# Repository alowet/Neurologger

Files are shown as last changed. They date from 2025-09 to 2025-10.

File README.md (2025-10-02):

## WILD: Wireless, Interactive, Lightweight Datalogger 

**WILD** (Wireless, Interactive, Lightweight Datalogger) is an open-source platform for **wireless, closed-loop electrophysiology and behavior monitoring** in freely moving small animals. It integrates high-density electrophysiology, optogenetic stimulation, an inertial measurement unit (IMU), ultrasonic microphone, and head-mounted camera into a lightweight system for **multi-modal recording**.

---

## 📌 Overview

- High-density neural recording  
- BLE-based wireless control and real-time monitoring  
- Closed-loop stimulation with DSP filtering and thresholds  
- SD-card logging in CE32 format with efficient data export  
- Windows GUI for device setup, live visualization, and data download  

---

## 📖 Documentation

Full documentation can be found here:

- [Installation](docs/install.md)  
- [Hardware](docs/hardware.md)
- [Usage Guide](docs/usage.md)  
- [Closed-loop Control](docs/closed-loop.md)
- [TinyML(Under development for supporting user-compiled models)](docs/tinyML.md)
- [File Format](docs/file-format.md)  
- [Development](docs/development.md)  

---

## 🖥 Quick start guide
WILD system board
WILD

Connector definitions
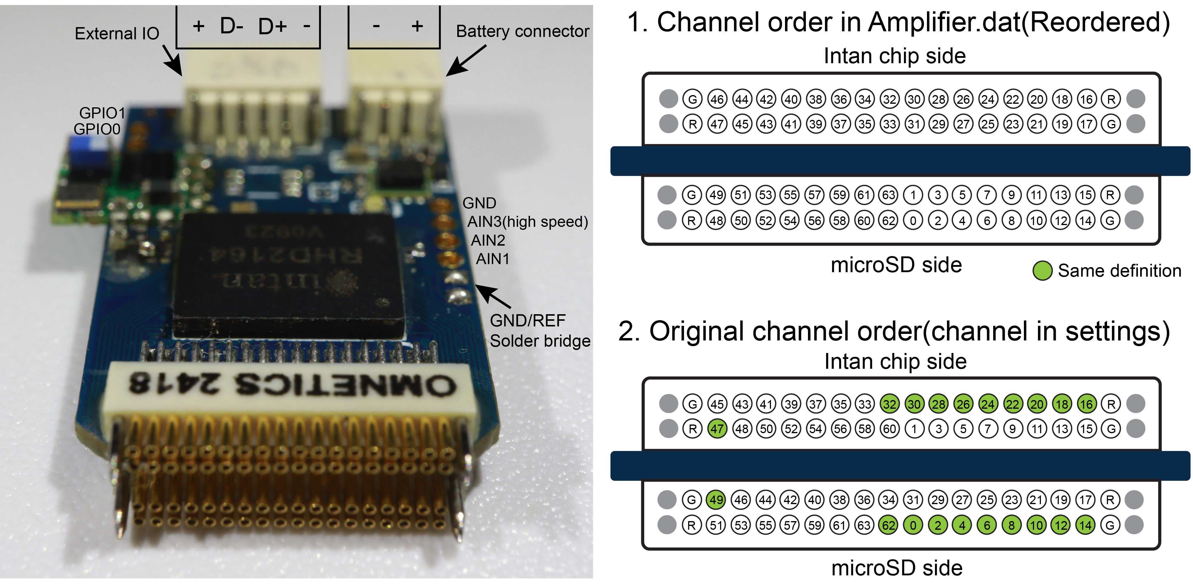
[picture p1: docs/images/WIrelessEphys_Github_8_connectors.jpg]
Connectors


WILD system diagram
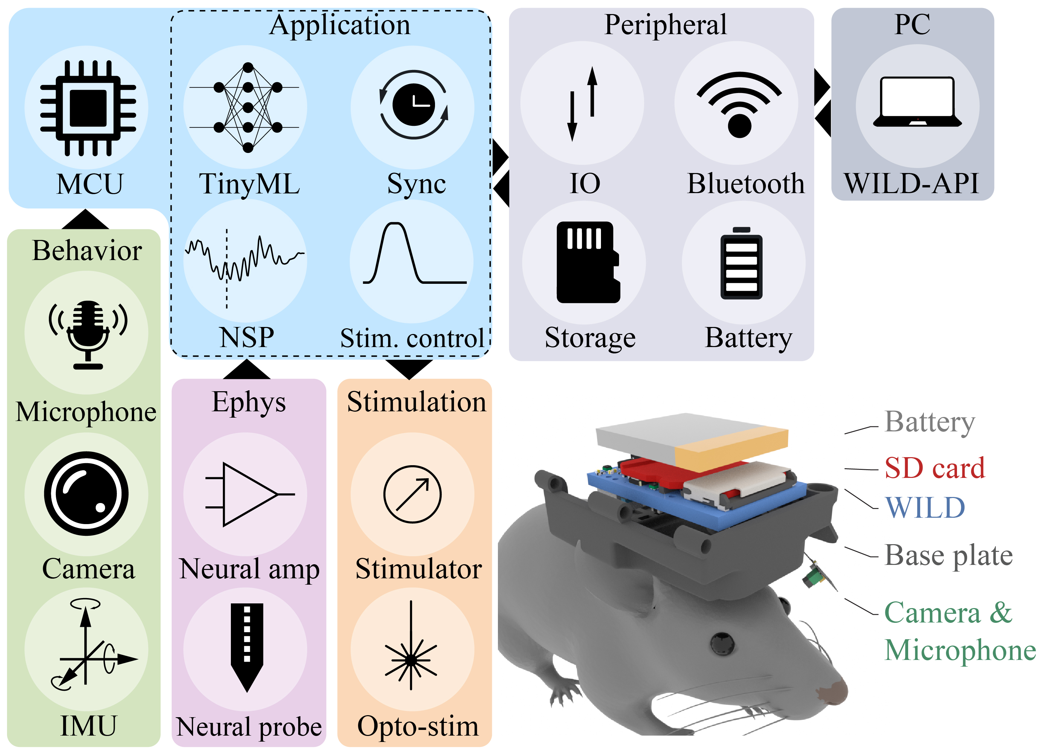
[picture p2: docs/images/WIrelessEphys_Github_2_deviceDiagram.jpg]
System schematics


### Device manufacturing
- PCB manufacturing and assembly (Gerber + BOM provided)
[Download here](https://github.com/ayalab1/Neurologger/tree/main/PCB)  
- Recommended PCB manufacturer: [NextPCB](https://www.nextpcb.com)
- 3D printed baseplate:   [Download here](https://github.com/ayalab1/Neurologger/tree/main/3Dprint)  

### Firmware programming (first time to empty MCU)
1. Connect 4-pin IO–USB cable (do not connect to PC yet).  
2. Short DFU model select pin to VDD(with a metal tweezer for shorting) to enter DFU mode.  
3. Connect USB cable to PC while shorting VDD and model select pin, once powered up, you can release the tweezer.  
4. In **STM32CubeProgrammer**, flash the bootloader firmware.  

### Preparing for recording
- Install WILD PC software:  
  [Download here](https://github.com/ayalab1/Neurologger/tree/main/Software)  
- Format microSD card in WILD PC software (CE32 format).
- Upload application image to SDcard, device will automatically upgrade during power-on from SDcard.
  [Download here](https://github.com/ayalab1/Neurologger/tree/main/Firmware)  
- Ensure battery is fully charged (check polarity on JST-SH2.0 connector).  

### Recording
- Ensure PC has Bluetooth 4.0+ enabled.  
- Connect wirelessly through GUI.  
- Start recording and monitor signals in real time.  

### Data downloading
- Use GUI **Download** function.  
- Files exported as: `amplifier.dat`, `analogin.dat`, `digitalin.dat`, `supply.dat`, `adc.dat`, `time.dat`, `info.rhd`, `CE_params.bin`.  
- Post-processing scripts including data formatting, video generation, sensor-fusions are provided.
[Download here](https://github.com/ayalab1/Neurologger/tree/main/Code)  
---

## ⚠️ Disclaimer

> DISCLAIMER – FOR INFORMATIONAL PURPOSES ONLY; USE AT YOUR OWN RISK  
>  
> The protocol content here is for informational purposes only and does not constitute legal, medical, clinical, or safety advice. Content added to protocols.io is not peer reviewed and may not have undergone formal approval. Information presented should not substitute for independent professional judgment. Any action you take using this information is strictly at your own risk. Neither the authors nor contributors are responsible for your use of the information.

---

## 🔧 Resources

- **Firmware & Embedded software**: Keil MDK, STM32CubeProgrammer  
- **PC GUI / API**: Visual Studio (C#)  
- **Machine learning integration**: Python, TensorFlow, ST Edge-AI  

---

## 📜 License

MIT License. See [LICENSE](LICENSE).

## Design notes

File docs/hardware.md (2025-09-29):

# Hardware

## WILD

## WILD opto-module

## WILD camera

## Cables
### Programming cable

### Sync cable

## microSD cards

## Batteries

## 3D print parts

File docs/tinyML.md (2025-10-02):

# Model-based computations(under development)
WILD supports online inference of pre-trained tensorflow-lite models.
Inference time is correlated to the model sizes.
Currently, the model is pre-compiled of the firmware, a run-time model loading mechanism is being developed.
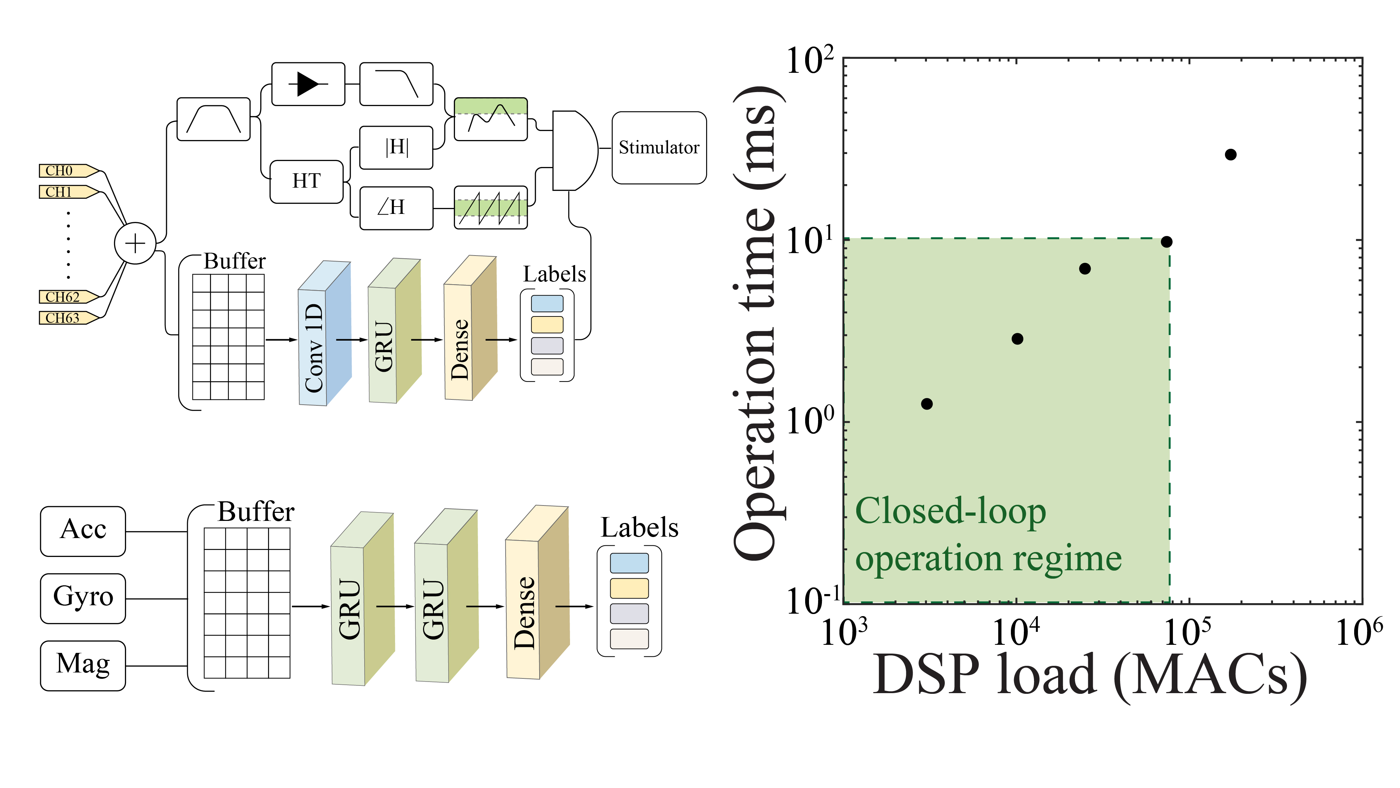
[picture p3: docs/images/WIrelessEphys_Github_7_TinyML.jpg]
TinyML


Sample scripts of model training/developing pipelines can be found here.

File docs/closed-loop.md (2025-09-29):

# Closed-loop Control

The system provides multiple DSP and stimulation modes for real-time closed-loop experiments.

## DSP Modes
- Disabled
- Single A
- Single A (Hilbert)
- Double
- Double (Hilbert)
- Cascade A→B
- Gated A & B
- Random
  
## Filters
One of the filter can be selected for one DSP channel (2 channels per system for now)
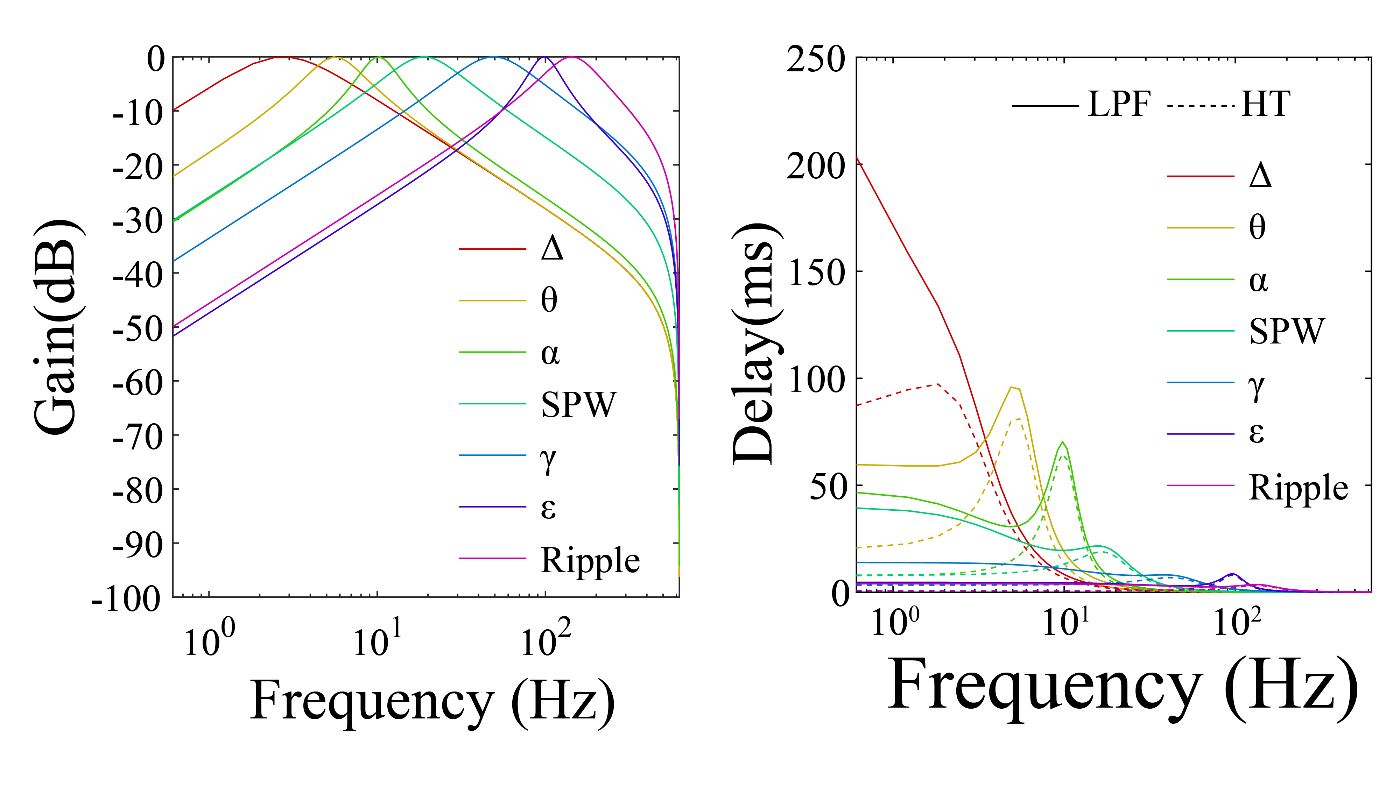
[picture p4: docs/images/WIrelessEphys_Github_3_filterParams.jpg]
CLOSED-LOOP Filters

- Delta
- Theta
- Alpha
- Beta
- Gamma
- Epsilon
- Ripple

## Arbitrary Referencing
- Direct (x = A)
- Differential (x = A − B)
- CSD (x = 2A − B − C)

## Stimulation
- Select stimulation channels (STIM1, STIM2)
- Configure pulse width, delay, frequency
- Enable random triggering

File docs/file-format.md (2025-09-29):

# File Format

Each recording session produces a folder with:

- `amplifier.dat` — neural signals (int16), sampling rate depends on recording settings.
- `analogin.dat` — auxiliary analog input,1250Hz, 16x 16-bit signals: Digital inputs/ AccX/AccY/AccZ/GyroX/GyroY/GyroZ/MagX/MagY/MagZ/32bit time/DSP1_in/DSP2_in/DSP1_out/DSP2_out
- `adc.dat` — ADC raw channels (for microphone, 160KHz sampling rate)
- `misc.dat` — Raw image data from camera
- `info.rhd` — Intan-compatible metadata
- `CE_params.bin` — system & DSP parameters

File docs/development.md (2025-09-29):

# Development & Contributing

## Repo Structure
- `CE32_console/` — Windows GUI
- `CE32_BLE/` — BLE communication
- `dll_upfirdn.dll` — resampling backend
- `docs/` — documentation site

## Contributing
We welcome issues and pull requests!

1. Fork the repo
2. Create a feature branch
3. Add tests and documentation
4. Submit PR

## License
MIT License. See [LICENSE](../LICENSE).

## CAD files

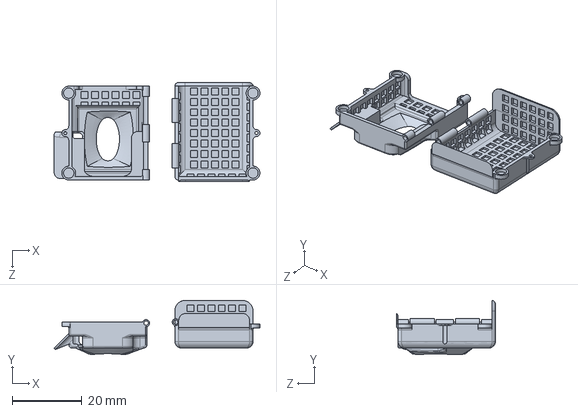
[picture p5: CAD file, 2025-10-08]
3Dprint/Wild_Case.SLDPRT
59.2 x 15.6 x 28.4 mm

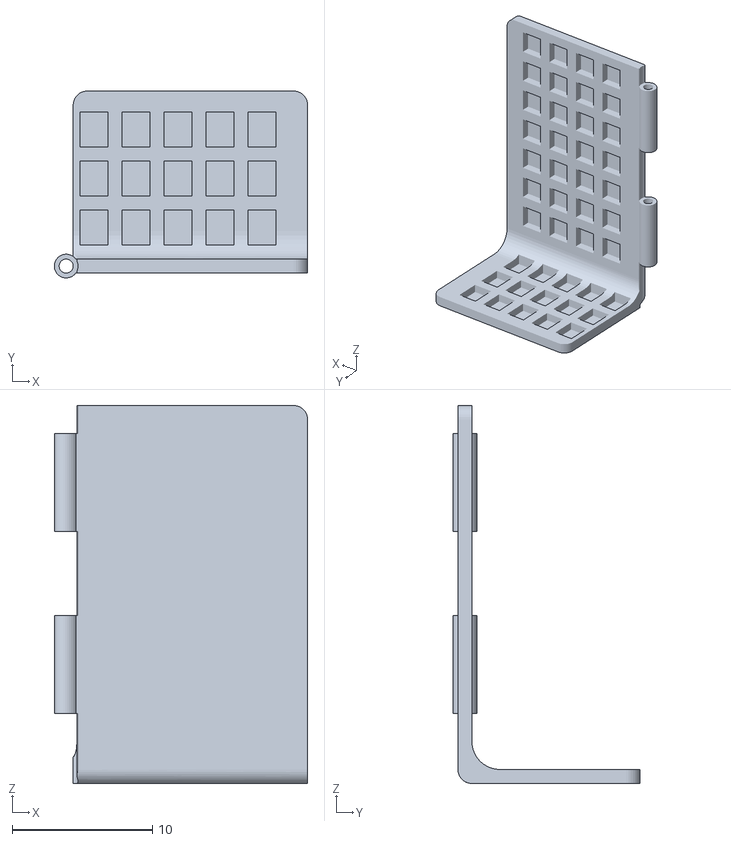
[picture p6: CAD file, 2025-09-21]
3Dprint/WILD_TopCover.STL
18.1 x 13.3 x 27.0

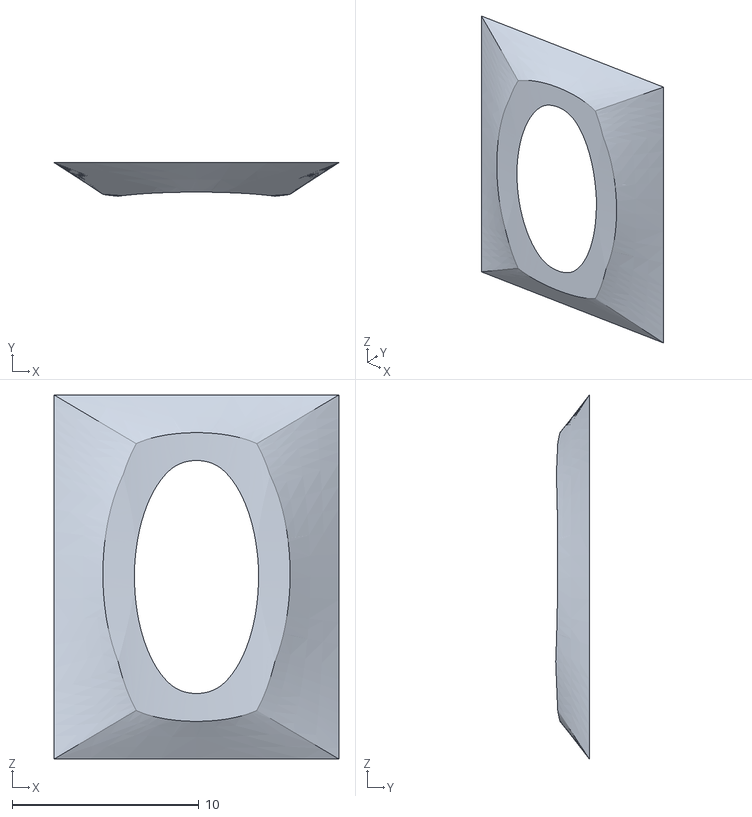
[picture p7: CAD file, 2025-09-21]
3Dprint/WILD_Baseplate.STL
15.2 x 1.80 x 19.5

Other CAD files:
3Dprint/WILD_Baseplate_Camera.STL
3Dprint/WILD_Case.f3d

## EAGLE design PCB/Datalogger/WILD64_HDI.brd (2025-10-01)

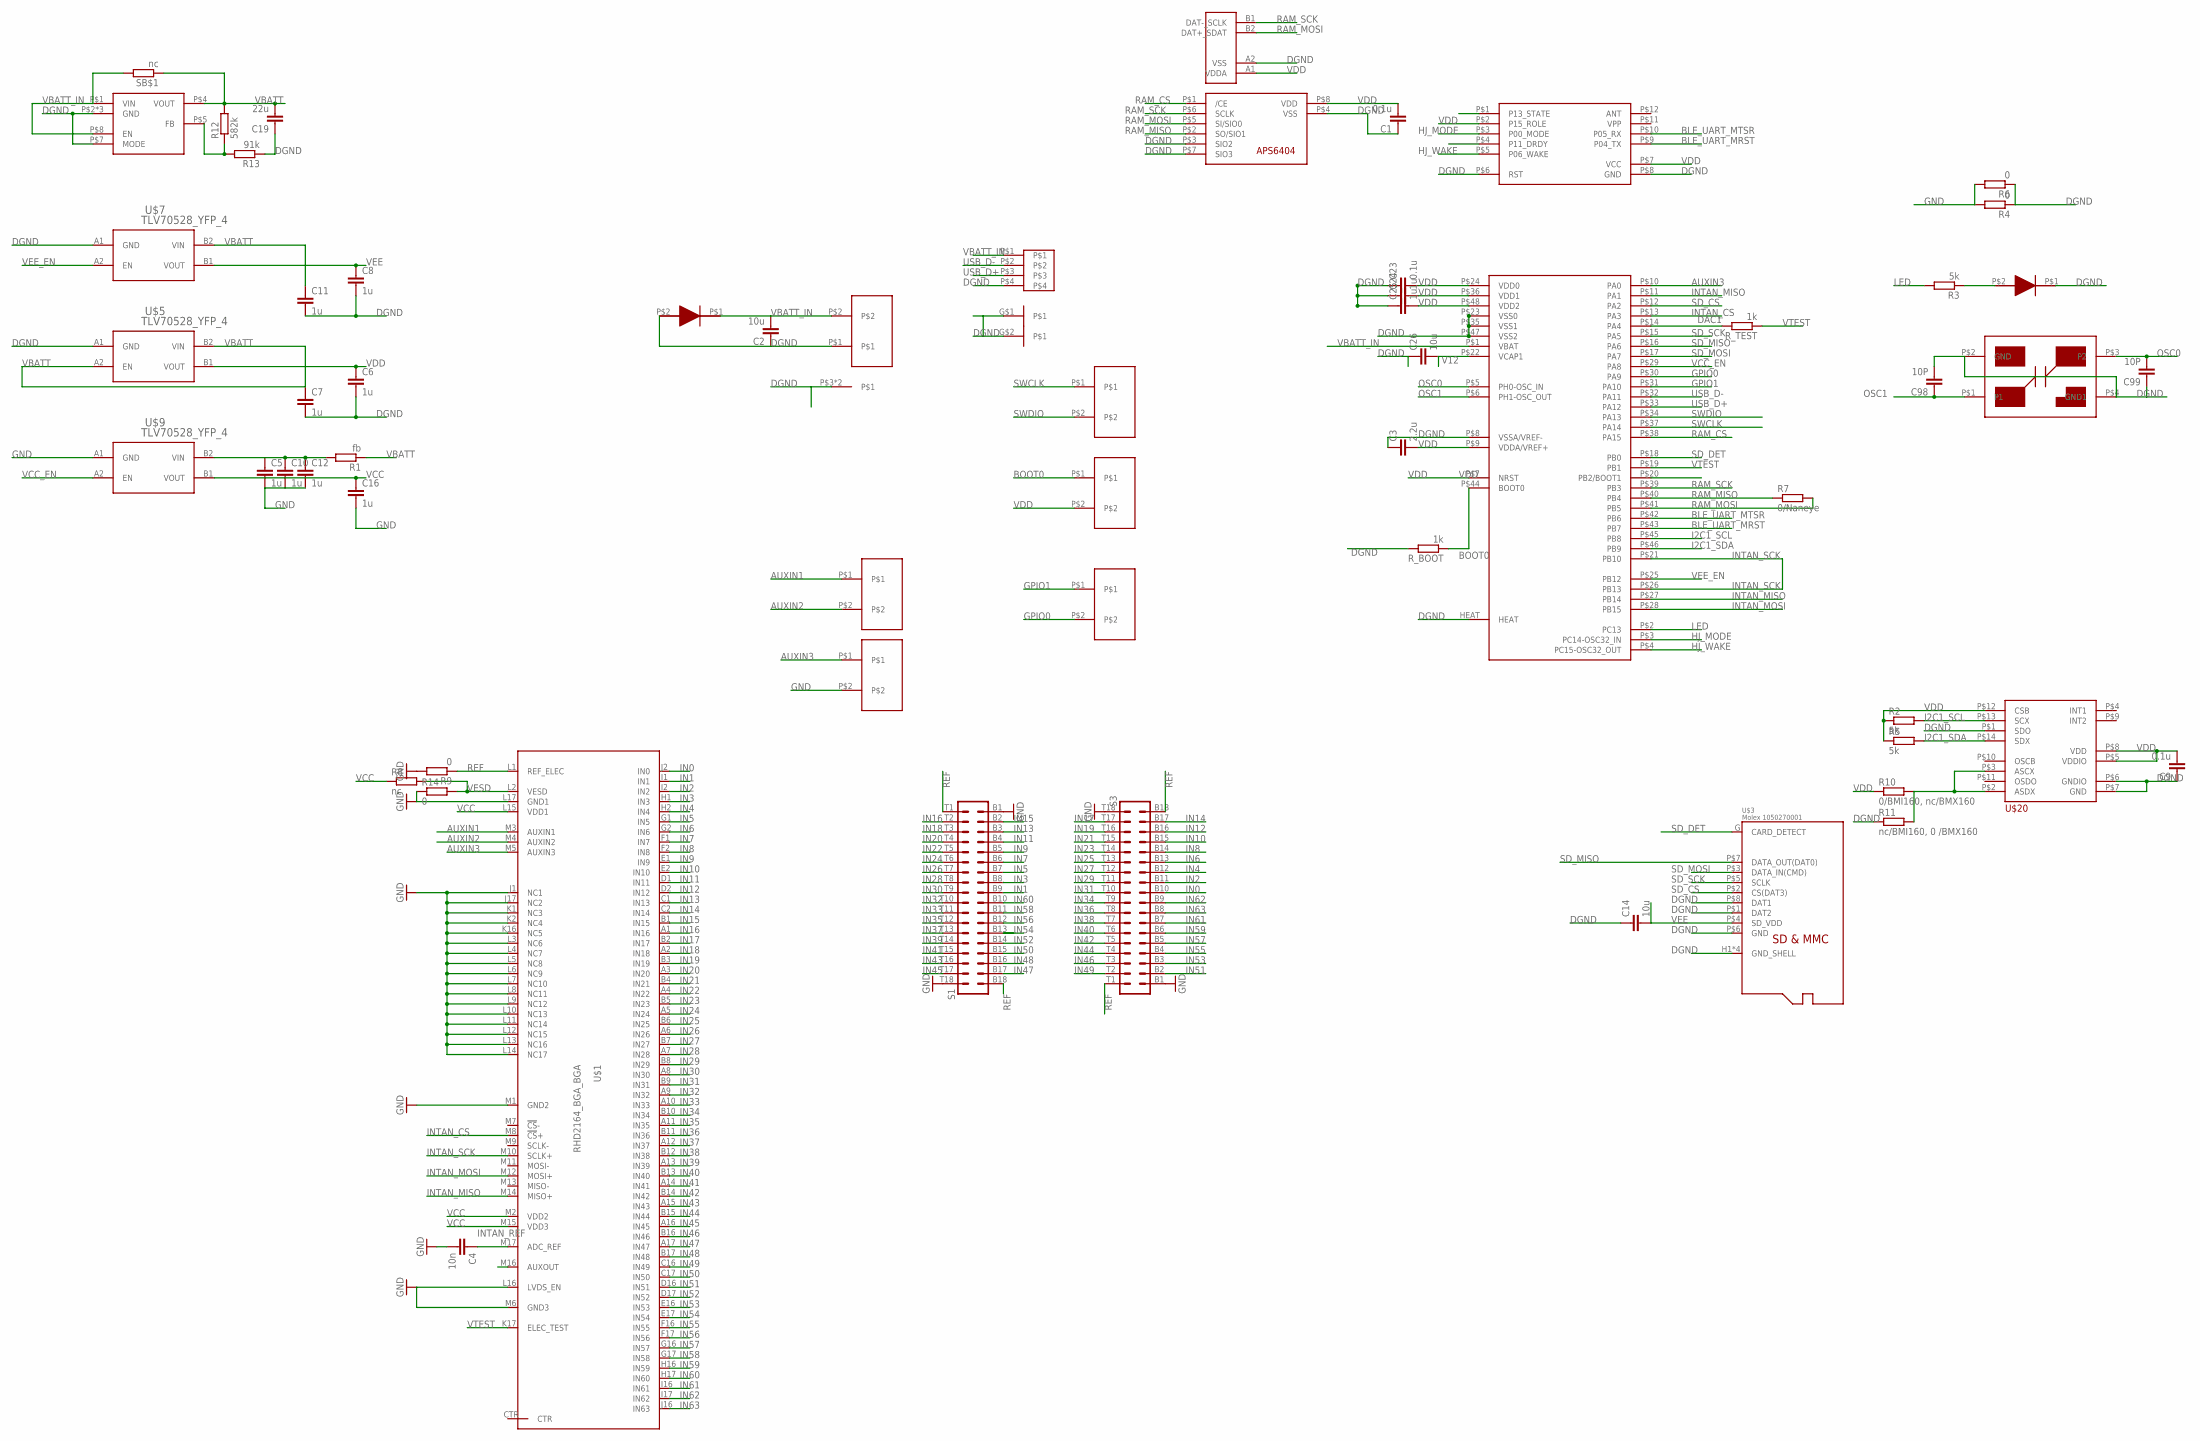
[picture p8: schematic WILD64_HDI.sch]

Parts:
C1, C9, C23: 0.1u; C0201
C2: 10u; 0402
C3: 2.2u; C0201
C4: 10n; C0201
C5, C6, C7, C8, C10, C11, C12, C16, C24, C25: 1u; C0201
C14, C26: 10u; C0402
C19: 22u; 0402
C98, C99: 10P; C0201
R1: fb; R0201
R2, R3, R5: 5k; R0201
R4, R6, R14: 0; R0201
R7: 0/Naneye; R0201
R8: nc; R0201
R9: 0; R0402
R10: 0/BMI160, nc/BMX160; R0201
R11: nc/BMI160, 0 /BMX160; R0201
R12: 582k; R0201
R13: 91k; R0201
R_BOOT: 1k; R0201
R_TEST: 1k; R0201
S1, S3: OMNETICS_A79025
SB$1: nc; R0201
U$1: RHD2164_BGA_BGA; BGA104_9X7
U$2: 1.0MM_1X2VIA; PIN_1.0MM_1X2
U$3: Molex 1050270001; MICROSD_SHORT_1.7H
U$4: NANEYECBGA; NANEYEC_4BGA
U$5, U$7, U$9: TLV70528_YFP_4; YFP4
U$6: STM32F411_QFN48; UFQFPN48
U$8, U$17, U$18, U$19: 1.27MM_1X2CONN; 1.27MM_1X2
U$10: HJ580
U$11, U$16: DIODE0402; 0402_LED
U$12: 1.0MM_1X4PAD; 1.0MM_CONN_1X4_SMD
U$13: 1.00MM_1X2PAD; 1.0MM_CONN_1X2_SMD
U$14: APS6404; USON-8L_3X2
U$15: ABM12_CRYSTAL; SMD4_1.6MMX1.2MM
U$20: BMI27014; 14_VFLGA
U$22: TPSM83100; MICROSIP_SIU0008A

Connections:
AUXIN1: U$1.M3 (AUXIN1), U$19.P$1
AUXIN2: U$1.M4 (AUXIN2), U$19.P$2
AUXIN3: U$1.M5 (AUXIN3), U$6.P$10 (PA0), U$18.P$1
AUXOUT: U$1.M16 (AUXOUT)
BLE_UART_MRST: U$6.P$43 (PB7), U$10.P$9 (P04_TX)
BLE_UART_MTSR: U$6.P$42 (PB6), U$10.P$10 (P05_RX)
BOOT0: R_BOOT.1, U$6.P$44 (BOOT0), U$8.P$1
DAC1: R_TEST.2, U$6.P$14 (PA4)
DGND: C1.1, C2.1, C3.1, C6.2, C7.2, C8.2, C9.1, C11.2, C14.1, C19.1, C23.1, C24.1, C25.1, C26.1, C98.2, C99.1, R4.1, R6.1, R11.1, R13.1, R_BOOT.2, U$3.H1 (GND_SHELL), U$3.H2 (GND_SHELL), U$3.H3 (GND_SHELL), U$3.H4 (GND_SHELL), U$3.P$1 (DAT2), U$3.P$6 (GND), U$3.P$8 (DAT1), U$4.A2 (VSS), U$5.A1 (GND), U$6.HEAT, U$6.P$8 (VSSA/VREF-), U$6.P$23 (VSS0), U$6.P$35 (VSS1), U$6.P$47 (VSS2), U$7.A1 (GND), U$10.P$6 (RST), U$10.P$8 (GND), U$11.P$2 (IN), U$12.G$1, U$12.G$2, U$12.P$4, U$13.P$1, U$13.P$3, U$13.P$4, U$14.P$3 (SIO2), U$14.P$4 (VSS), U$14.P$7 (SIO3), U$15.P$2 (GND), U$15.P$4 (GND1), U$16.P$1 (OUT), U$20.P$1 (SDO), U$20.P$6 (GNDIO), U$20.P$7 (GND), U$22.P$2 (GND), U$22.P$3 (GND), U$22.P$6 (GND), U$22.P$7 (MODE)
GND: C4.2, C5.2, C10.2, C12.2, C16.2, R4.2, R6.2, R9.2, R14.1, S1.B1, S1.T18, S3.B1, S3.T18, U$1.J1 (NC1), U$1.J17 (NC2), U$1.K1 (NC3), U$1.K2 (NC4), U$1.K16 (NC5), U$1.L3 (NC6), U$1.L4 (NC7), U$1.L5 (NC8), U$1.L6 (NC9), U$1.L7 (NC10), U$1.L8 (NC11), U$1.L9 (NC12), U$1.L10 (NC13), U$1.L11 (NC14), U$1.L12 (NC15), U$1.L13 (NC16), U$1.L14 (NC17), U$1.L16 (LVDS_EN), U$1.L17 (GND1), U$1.M1 (GND2), U$1.M6 (GND3), U$9.A1 (GND), U$18.P$2
GPIO0: U$6.P$30 (PA9), U$17.P$2
GPIO1: U$6.P$31 (PA10), U$17.P$1
HJ_MODE: U$6.P$3 (PC14-OSC32_IN), U$10.P$3 (P00_MODE)
HJ_WAKE: U$6.P$4 (PC15-OSC32_OUT), U$10.P$5 (P06_WAKE)
I2C1_SCL: R2.2, U$6.P$45 (PB8), U$20.P$13 (SCX)
I2C1_SDA: R5.2, U$6.P$46 (PB9), U$20.P$14 (SDX)
IN0: S3.B10, U$1.J2 (IN0)
IN1: S1.B9, U$1.I1 (IN1)
IN2: S3.B11, U$1.I2 (IN2)
IN3: S1.B8, U$1.H1 (IN3)
IN4: S3.B12, U$1.H2 (IN4)
IN5: S1.B7, U$1.G1 (IN5)
IN6: S3.B13, U$1.G2 (IN6)
IN7: S1.B6, U$1.F1 (IN7)
IN8: S3.B14, U$1.F2 (IN8)
IN9: S1.B5, U$1.E1 (IN9)
IN10: S3.B15, U$1.E2 (IN10)
IN11: S1.B4, U$1.D1 (IN11)
IN12: S3.B16, U$1.D2 (IN12)
IN13: S1.B3, U$1.C1 (IN13)
IN14: S3.B17, U$1.C2 (IN14)
IN15: S1.B2, U$1.B1 (IN15)
IN16: S1.T2, U$1.A1 (IN16)
IN17: S3.T17, U$1.B2 (IN17)
IN18: S1.T3, U$1.A2 (IN18)
IN19: S3.T16, U$1.B3 (IN19)
IN20: S1.T4, U$1.A3 (IN20)
IN21: S3.T15, U$1.B4 (IN21)
IN22: S1.T5, U$1.A4 (IN22)
IN23: S3.T14, U$1.B5 (IN23)
IN24: S1.T6, U$1.A5 (IN24)
IN25: S3.T13, U$1.B6 (IN25)
IN26: S1.T7, U$1.A6 (IN26)
IN27: S3.T12, U$1.B7 (IN27)
IN28: S1.T8, U$1.A7 (IN28)
IN29: S3.T11, U$1.B8 (IN29)
IN30: S1.T9, U$1.A8 (IN30)
IN31: S3.T10, U$1.B9 (IN31)
IN32: S1.T10, U$1.A9 (IN32)
IN33: S1.T11, U$1.A10 (IN33)
IN34: S3.T9, U$1.B10 (IN34)
IN35: S1.T12, U$1.A11 (IN35)
IN36: S3.T8, U$1.B11 (IN36)
IN37: S1.T13, U$1.A12 (IN37)
IN38: S3.T7, U$1.B12 (IN38)
IN39: S1.T14, U$1.A13 (IN39)
IN40: S3.T6, U$1.B13 (IN40)
IN41: S1.T15, U$1.A14 (IN41)
IN42: S3.T5, U$1.B14 (IN42)
IN43: S1.T16, U$1.A15 (IN43)
IN44: S3.T4, U$1.B15 (IN44)
IN45: S1.T17, U$1.A16 (IN45)
IN46: S3.T3, U$1.B16 (IN46)
IN47: S1.B17, U$1.A17 (IN47)
IN48: S1.B16, U$1.B17 (IN48)
IN49: S3.T2, U$1.C16 (IN49)
IN50: S1.B15, U$1.C17 (IN50)
IN51: S3.B2, U$1.D16 (IN51)
IN52: S1.B14, U$1.D17 (IN52)
IN53: S3.B3, U$1.E16 (IN53)
IN54: S1.B13, U$1.E17 (IN54)
IN55: S3.B4, U$1.F16 (IN55)
IN56: S1.B12, U$1.F17 (IN56)
IN57: S3.B5, U$1.G16 (IN57)
IN58: S1.B11, U$1.G17 (IN58)
IN59: S3.B6, U$1.H16 (IN59)
IN60: S1.B10, U$1.H17 (IN60)
IN61: S3.B7, U$1.I16 (IN61)
IN62: S3.B9, U$1.I17 (IN62)
IN63: S3.B8, U$1.J16 (IN63)
INTAN_CS: U$1.M8 (!CS!+), U$6.P$13 (PA3)
INTAN_MISO: U$1.M14 (MISO+), U$6.P$11 (PA1), U$6.P$27 (PB14)
INTAN_MOSI: U$1.M12 (MOSI+), U$6.P$28 (PB15)
INTAN_REF: C4.1, U$1.M17 (ADC_REF)
INTAN_SCK: U$1.M10 (SCLK+), U$6.P$21 (PB10), U$6.P$26 (PB13)
LED: R3.2, U$6.P$2 (PC13)
unnamed: R10.2, R11.2, U$20.P$2 (ASDX), U$20.P$3 (ASCX)
unnamed: R12.1, R13.2, U$22.P$5 (FB)
unnamed: R3.1, U$16.P$2 (IN)
OSC0: C99.2, U$6.P$5 (PH0-OSC_IN), U$15.P$3 (P2)
OSC1: C98.1, U$6.P$6 (PH1-OSC_OUT), U$15.P$1 (P1)
RAM_CS: U$6.P$38 (PA15), U$14.P$1 (/CE)
RAM_MISO: R7.1, U$6.P$40 (PB4), U$14.P$2 (SO/SIO1)
RAM_MOSI: R7.2, U$4.B2 (DAT+_SDAT), U$6.P$41 (PB5), U$14.P$5 (SI/SIO0)
RAM_SCK: U$4.B1 (DAT-_SCLK), U$6.P$39 (PB3), U$14.P$6 (SCLK)
REF: R9.1, S1.B18, S1.T1, S3.B18, S3.T1, U$1.L1 (REF_ELEC)
SD_CS: U$3.P$2 (CS(DAT3)), U$6.P$12 (PA2)
SD_DET: U$3.G (CARD_DETECT), U$6.P$18 (PB0)
SD_MISO: U$3.P$7 (DATA_OUT(DAT0)), U$6.P$16 (PA6)
SD_MOSI: U$3.P$3 (DATA_IN(CMD)), U$6.P$17 (PA7)
SD_SCK: U$3.P$5 (SCLK), U$6.P$15 (PA5)
SWCLK: U$2.P$1, U$6.P$37 (PA14)
SWDIO: U$2.P$2, U$6.P$34 (PA13)
USB_D+: U$6.P$33 (PA12), U$12.P$3
USB_D-: U$6.P$32 (PA11), U$12.P$2
V12: C26.2, U$6.P$22 (VCAP1)
VBATT: C7.1, C11.1, C19.2, R1.1, R12.2, SB$1.1, U$5.A2 (EN), U$5.B2 (VIN), U$7.B2 (VIN), U$22.P$4 (VOUT)
VBATT_IN: C2.2, SB$1.2, U$6.P$1 (VBAT), U$11.P$1 (OUT), U$12.P$1, U$13.P$2, U$22.P$1 (VIN), U$22.P$8 (EN)
VCC: C16.1, R8.1, U$1.L15 (VDD1), U$1.M2 (VDD2), U$1.M15 (VDD3), U$9.B1 (VOUT)
VCC_EN: U$6.P$29 (PA8), U$9.A2 (EN)
VCC_LPF: C5.1, C10.1, C12.1, R1.2, U$9.B2 (VIN)
VDD: C1.2, C3.2, C6.1, C9.2, C23.2, C24.2, C25.2, R2.1, R5.1, R10.1, U$4.A1 (VDDA), U$5.B1 (VOUT), U$6.P$7 (NRST), U$6.P$9 (VDDA/VREF+), U$6.P$24 (VDD0), U$6.P$36 (VDD1), U$6.P$48 (VDD2), U$8.P$2, U$10.P$2 (P15_ROLE), U$10.P$7 (VCC), U$14.P$8 (VDD), U$20.P$5 (VDDIO), U$20.P$8 (VDD), U$20.P$12 (CSB)
VEE: C8.1, C14.2, U$3.P$4 (SD_VDD), U$7.B1 (VOUT)
VEE_EN: U$6.P$25 (PB12), U$7.A2 (EN)
VESD: R8.2, R14.2, U$1.L2 (VESD)
VTEST: R_TEST.1, U$1.K17 (ELEC_TEST), U$6.P$19 (PB1)

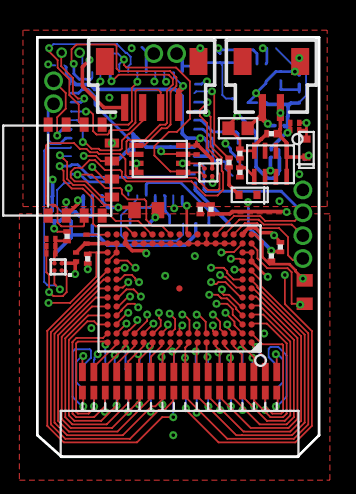
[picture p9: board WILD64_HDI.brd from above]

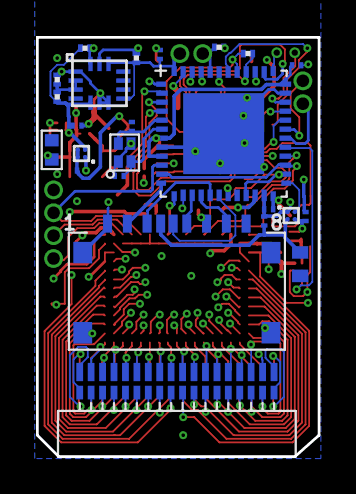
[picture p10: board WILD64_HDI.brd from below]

Board: 4 copper layers, 15.7 x 23.3 mm, 61 parts (26 on the bottom side), 115 nets.

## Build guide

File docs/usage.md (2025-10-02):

# Usage Guide
## Pre-recording preparations
1. Prepare/Recharge battery
WILD integrated a DC/DC buck/boost converter and receive a wide input range from 2V-4.5V. Battery needs to ensure a minimal power required by the recording mode. Battery needs to supply >30mW peak power during booting.
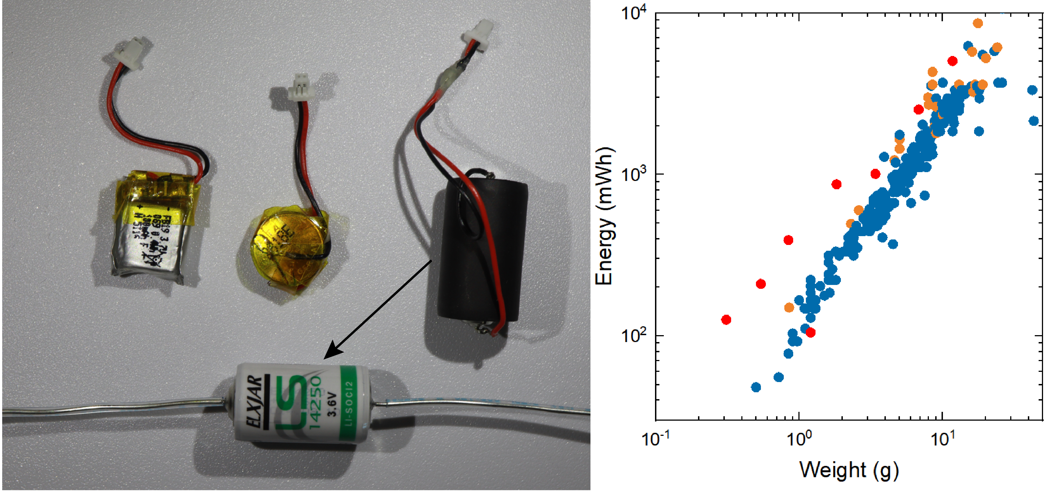
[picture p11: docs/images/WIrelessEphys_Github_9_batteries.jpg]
Battery

[Battery selection table](https://github.com/ayalab1/Neurologger/tree/main/docs/LipoBattery_selection.csv)  
2. Format SD card using WILD_console. *Make sure WILD_console has Admin priviliage. Sandisk microSDs may not be supported, we recommend Samsung EVO series(orange) or Lexar card. Avoid using high-speed SDcard as they consume much more power.
Power consumption could be largely impacted by the microSD make.
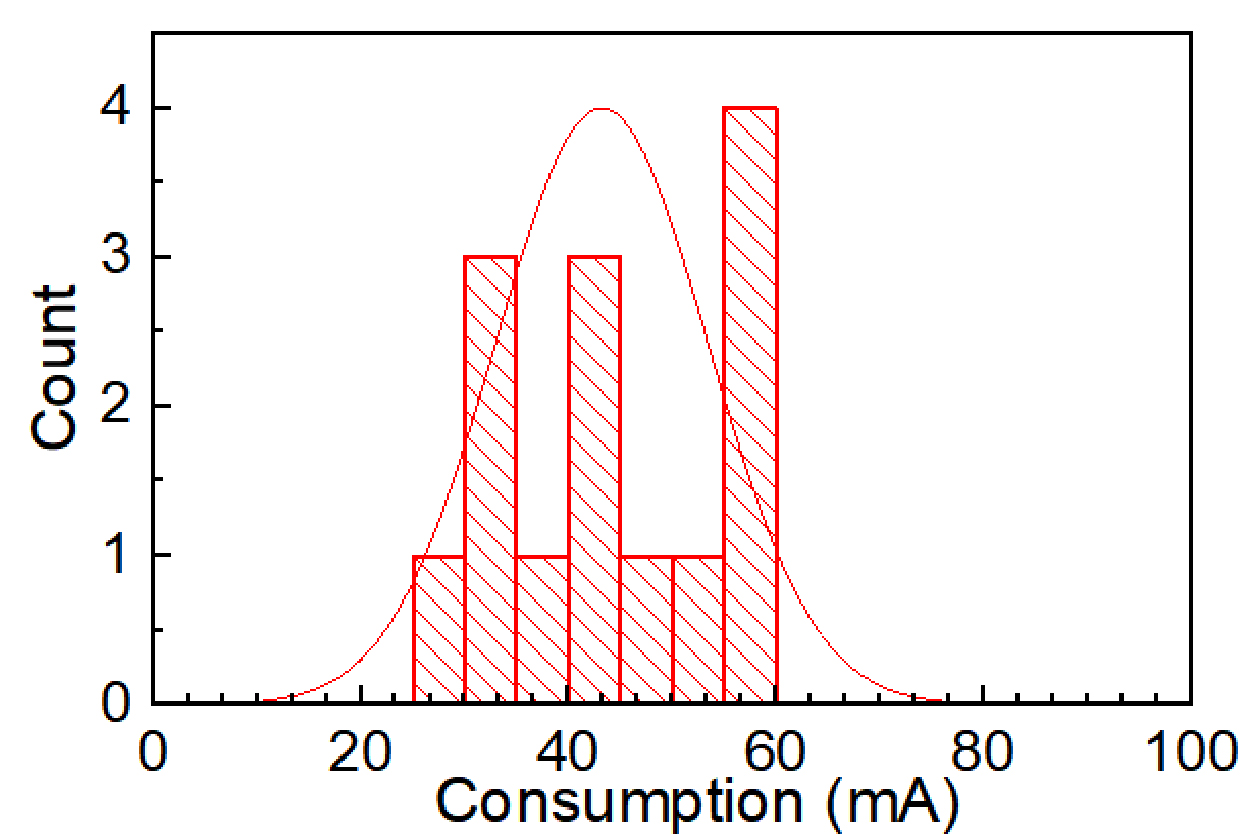
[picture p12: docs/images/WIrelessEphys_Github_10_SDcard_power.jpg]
SDcard

3. Insert SD card to WILD.
4. Connect battery. Device will start booting, a Blue LED will be on, indicating device started Ok and goes off to enter low power mode. If a firmware loaded to SD card, device will check the firmware image and start upgrading (LED will blink, it will take ~10s depends on the size of image).
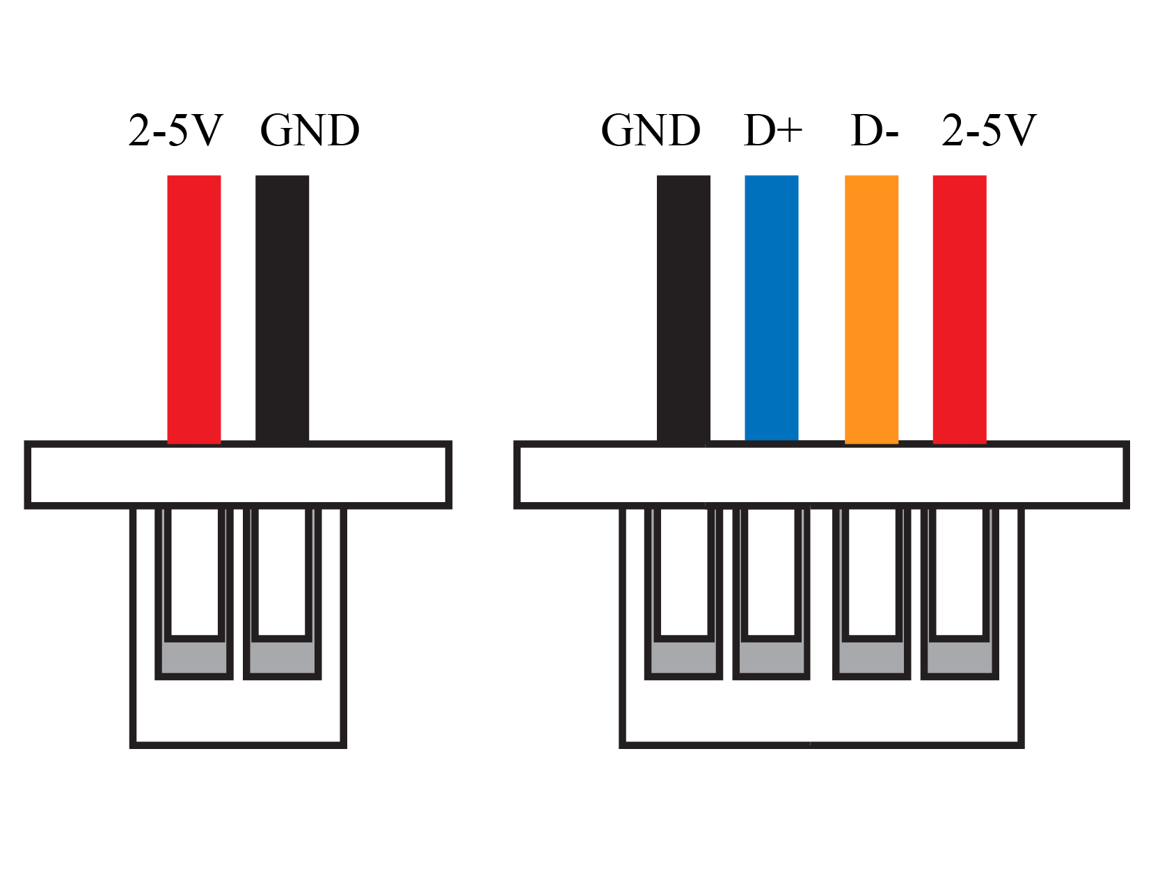
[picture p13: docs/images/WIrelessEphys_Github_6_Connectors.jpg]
IO config


## Connecting
1. Launch **WILD_console.exe**
2. Select device in **Port** dropdown (BLE scan).
3. Connect, wait for synchronization, a number on the bottom of the panel will increase indicating communication successful.
   *If connection is successful and syncrhonization is not started (TX number does not increase), may indicate a SDcard issue.

## Recording
1. Configure closed-loop function in Closed-loop panel
2. Configure recording speed with Custom speed drop-box
3. If need to start multiple device around same time, click **Wait for start**, will wait for other WILD_console instance without this option checked (<50ms bluetooth jitter, however, timestamp of recording start time is recorded based on calibrated high-precision clock)
4. Click **Recording Start**. Data will be start streaming in 1 second. 
5. Click **Recording Stop** after experiment finished. If battery died during the recording, the recording files will not be lost.
   
## Real-time Display
- When recording start, preview data streaming is enabled by default. Preview channels can be selected by selecting **Display Channel** or **Display Auxilary** for additional signals from IMU, DSP.
- Preview can be turned off to save power (~0.5mA) and save host-BLE bandwidths. 
- Internal state display: Shows real-time internal signals including closed-loop detection, stimulation trigger, DSP states.
- Adjustable display length: 1s, 2s, 5s, 10s
- Adjustable gain: 10 µV – 5 mV
- Threshold overlays available during closed-loop (if switched to corresponding DSP channels)
- States display device messages. TinyML model states will be shown here.
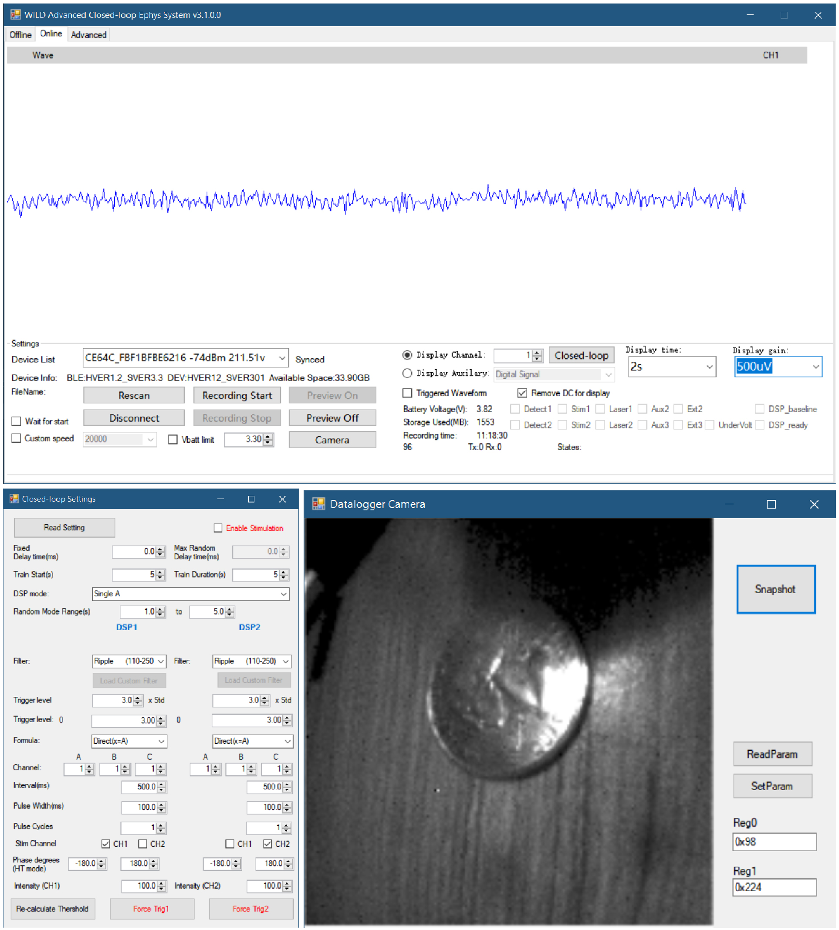
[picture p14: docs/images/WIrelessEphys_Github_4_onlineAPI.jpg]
RealTimeControl


## Data Downloading
1. Insert SD card
2. Click **Save to Disk** and select the target folder. Data will be organized by recording ID and timestamp of recording start time.
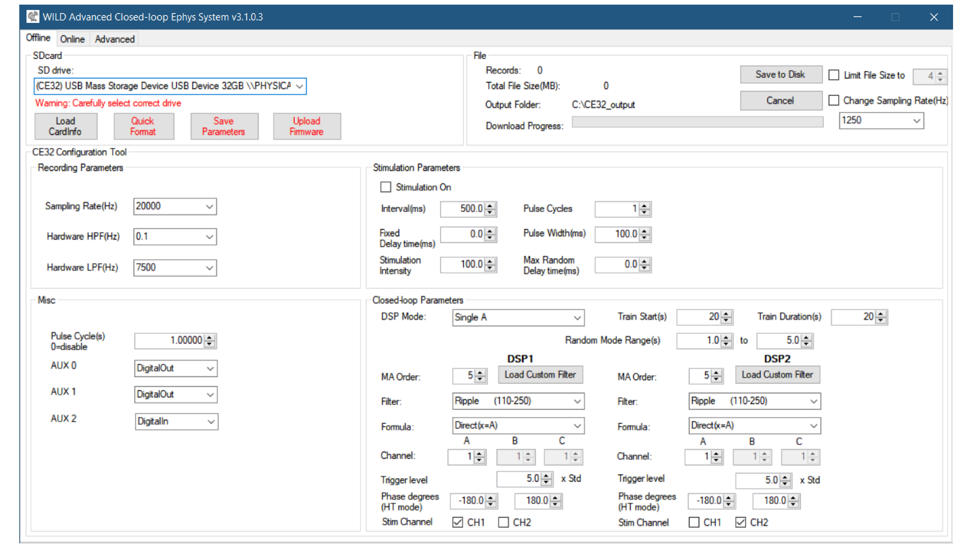
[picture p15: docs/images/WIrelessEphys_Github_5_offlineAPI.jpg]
OfflineInterface


## Post Processing
We have provided several processing scripts for post-processing data.
[Download here](https://github.com/ayalab1/Neurologger/tree/main/Code)  
1. To ensure the data format is consistant with conventional recording systems, naming convention and files are organized in a similar manner with Intan RHD2000 system. However, a post downloading process is still required for generating correct header and time.dat. Run WILD_PreProcess.m for this correc
ion. This will generate FMAToolbox style event files based on the digital input signal.
2. For recordings with camera, video file is stored in misc.dat in uncompressed binary file. Video decoding and post-processing can be performed with WILD_VideoDecodewAudio.py.
3. For sensor fusion of IMU data, run WILD_processIMU.m

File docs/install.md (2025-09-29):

# WILD API Installation

## Requirements
- Windows 10 or later
- .NET Framework 4.8
- Visual Studio 2022 (recommended)

## Steps

1. Clone the repository:
   ```bash
   git clone https://github.com/ayalab1/Neurologger
   cd Neurologger
   ```
2. Navigate to /Neurologger/Software and install the latest installation package

## For development
1. Open the solution in Visual Studio.
2. Restore NuGet packages and build.

## Dependencies
- Windows.Devices.Bluetooth
- System.Windows.Forms
- Microsoft.Win32.SafeHandles

## Optional DLLs
- `dll_upfirdn.dll` — resampling
- `CE32_BLE.dll` — BLE backend

Place DLLs in the same folder as `CE32_console.exe`.

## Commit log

2025-09-21 PCB manufactoring file uploads
    [copper_bottom.gbr, copper_bottom_l4.gbr, copper_inner_l2.gbr, copper_inner_l3.gbr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]
2025-09-21 3D print file submitted
    [WILD_Baseplate.STL, WILD_Baseplate_Camera.STL, WILD_TopCover.STL]
2025-09-29 Added camera mode application file
2025-09-30 EaglePCB files of datalogger uploaded
    [WILD64_HDI.brd, WILD64_HDI.sch]
2025-10-01 Updated battery for usage
2025-10-01 Updated power consumption of sd card and lithium battery list
    [LipoBattery_selection.csv]
2025-10-08 Upload original designs of 3D print case
    [WILD_Case.f3d, Wild_Case.SLDPRT]
